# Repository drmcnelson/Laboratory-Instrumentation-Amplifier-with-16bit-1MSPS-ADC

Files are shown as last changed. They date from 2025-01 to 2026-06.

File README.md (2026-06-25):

# Laboratory Instrumentation Amplifier with bipolar inputs, 16bit 1MSPS ADC, SPI for Teensy, Arduino

<p align="center">
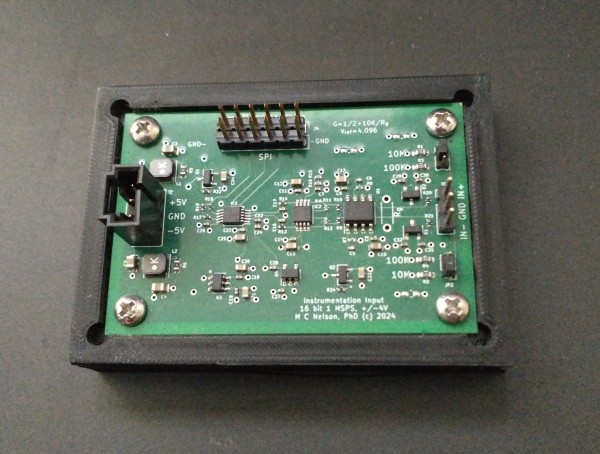
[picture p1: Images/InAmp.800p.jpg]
INA_actual

</p>

By [Dr M. C. Nelson](https://github.com/drmcnelson/Laboratory-Instrumentation-Amplifier-with-16bit-1MSPS-ADC),  [Copyright 2020-2026](LICENSE)

> **Important Build Note:** To ensure performance and alignment with the validated hardware and firmware, please build only from the **[Original Repository](https://github.com/drmcnelson/Laboratory-Instrumentation-Amplifier-with-16bit-1MSPS-ADC)**. 
>
>  For technical assistance or commercial inquiries, please contact me. I do my best to answer emails as volume allows.
<br>

---
### Table of contents
[Introduction](#intro)<br>
[1. Contents and instructions](#repo)<br>
[2. Design details](#design)<br>
[3. Spice model](#spice)<br>
[4. ADC sampling and timing](#timing)<br>
[5. Detailed part selection](#parts)<br>
[6. PCBWay sponsorship and acknowledgement](#ack)<br>

---
<br>

## Introduction

Instrumentation amplifiers ("INAs") are important for making sensitive precise stable voltage measurements with very high input impedance and strong noise rejection.
If you do research in the physical sciences or engineering or study electrical phenomena in biological systems, then you have probably used an INA.
They are a cornerstone of traditional instruments such as electrometers, and EKG machines, and laboratory studies in chemical physics, semiconductors, advanced materials, organo- and bio- electronics.

But, if you have used a traditional INA in your research, you may have noticed that they have certain limitations (which we are going to address in this design).
In particular, there is a well known trade-off where precision or sensitivity comes at the expense of some combination of bandwidth and impedance.
INAs are typically low bandwidth devices.
But there are interesting phenomena, for example involving charge processes on microsecond time scales, where high impedance measurements with a fast INA would be an especially useful tool.

This limitation in traditional INAs arises, at least in part, in two properties of amplifier chips; the input voltage noise density e<sub>n</sub> (V/√Hz) and the input current noise density i<sub>n</sub> (A/√Hz).
At a given bandwidth and impedance these contribute to the noise as *v*<sub>e,rms</sub> ≈ e<sub>n</sub>√f and *v*<sub>i,rms</sub> ≈ z<sub>n</sub> i<sub>n</sub> √f.
Note that both have a factor of root frequency but the current noise density is also multiplied by impedance.
We can think of a "noise resistance", R<sub>n</sub> = e<sub>n</sub>/i<sub>n</sub>.
When the amplifier input sees an impedance larger than R<sub>n</sub>, current noise dominates and noise increases more rapidly with bandwidth.
Low noise with high impedance and bandwidth requires low noise density with high noise resistance, alongside adequate bandwidth and slew.

Let's illustrate this with a numerical example. If we want 16 bit data for a signal of 1V, the noise (rms) should be around 10μV or smaller.
For a bandwidth of 1MHz, we need e<sub>n</sub> ≈ 10nV/√Hz.
And for an impedance of 10Mohm, we need i<sub>n</sub>  ≈ 1fA/√Hz.
That is, we need current noise density in the range of single digit fA/√Hz, or smaller.
It is challenging to find what we need in older INA chips (see [Table 5.8 in H&H AOE 3rd ed.](https://archive.org/details/the-art-of-electronics-3rd-ed-2015_202008/page/363/mode/1up)),
But there *are* newer Op Amps with ~10nV/√Hz and ~1fA/√Hz noise densities, >MHZ bandwidth and >10V/μs slew.
So, this is where a "roll your own" approach can be an advantage over older INA chips.

Another issue in traditional INAs is that they most often have single ended outputs.
The modern paradigm in high performance analog to digital converters (ADC) is increasingly to have differential inputs.
And, there is a large repertoire of high performance fully differential amplifiers (FDA) designed specifically to drive these differential ADCs.
Rather than run a single ended BNC across the lab to an analog input in a crate, nowadays we interface our high performance analog circuit over a short differential path to a high performance ADC co-located on the same board and export an all digital interface to an inexpensive microcontroller board or a computer.
The analog noise is well managed within a small area of the circuit board, and an all differential signal path helps control noise all the way to the ADC with its digital interface.

### About the INA and other contents of this repository:

In this repository we provide cad files and software source codes to make and operate an up-to-date instrumentation amplifier (INA) that can accommodate 10Mohm impedances with 16 bit precision at 1MSPS.
The host interface is a simple convert (CNVST) signal and SPI.
Asserting the "CNVST" line initiates conversion to digital and
after 700 nsecs, with CNVST low, a 16 bit SPI transfer retrieves the data.
The logic level for the SPI and CNVST are per the Vdd pin in the external connector and can be between 1.7V to 5.5V.
The SPI can be clocked as fast as 100MHz.
The INA board must be powered at -5V and +5V.
We provide a dual power supply for this, which we describe later.

We include an Arduino "sketch" (as source code) to operate the INA from a Teensy or Arduino microcontroller (MCU) board, and a Python program to provide an interactive interface to operate the instrument and record and display data in real time from a desktop or laptop computer.
The MCU board appears as a serial device to the computer with human readable commands and responses.
The source code has been compiled for and run on a Teensy 4, an Arduino UNO R4 and a STM32 Nucleo 144 (F7).
We prefer the Teensy for having the best SPI implementation and the fastest USB.

As described below, the basic operation of the device is simple and it should be easy to customize or crib from the source code or python code to integrate the INA into your experiment.

In the following we include some discussion of the design process, especially as related to part selection.
And we provide spice models that may help you check your changes, if you want to make any changes to the design.

For a more thorough discussion of the electrical topics mentioned here, the reader is referred to Horowitz, P., & Hill, W. (2015). The art of electronics (3rd ed.). Cambridge University Press. ISBN-10 0521809266.  Especially see Chapter 5 "Precision Circuits" and Chapter 8 "Low Noise Techniques".

### A word on the Spi Instrumentation Project:

Building instruments is an old tradition in science.  Many of the great advances were by scientists working with instrument makers or who were themselves great instrument makers.  In recent decades there is a different kind of pressure on academic science.  There seems to be less time or interest for learning those kinds of skills, compared to writing proposals to buy equipment.
Consequently doing science has become much more expensive and the sort of science someone gets to do increasingly becomes a function of where they are.
But like many things in nature, science is cyclic, and scientists are resourceful.
With the advent of low cost high performance MCU boards, 3-d printers and low cost CNC machines, there is now a growing community in DIY lab equipment.
But, there is still a roadblock when it comes to some of the more advanced design challenges.
Few are able to build a photon tagging system with picosecond timing from scratch, for example.
Our contribution, as long time instrumentation physicists is to fill in the gap to make higher end capabilities available to this new paradigm.
We believe that combining high end instrumentation circuits with the new generation in Arduino type MCU boards can be a powerful tool that can bring important capabilities to your lab and contribute to truly open science.

There is a sponsor button at the top of this repository.  Please do consider joining with us and contributing to our effort.

### Our sponsor for the INA - [PCBWay](https://www.pcbway.com/) 

We want to express special appreciation to PCBWay for sponsoring assembly of the first INA boards.  I enjoyed working them and we plan to work with PCBWay going forward.  Going back to PCBWay for the next designs and contributing to their community project forum, really is the best kind of praise that I can muster for any vendor.

On that note, we plan to post this design to the PCBWay community forum as our first experiment in this paradigm.  We are eager to see how it works out.

### Obtaining boards:

To obtain boards, the options include ordering a board through PCBWay per the above, or contact me and then click the sponsor button.
The parts cost at Digikey is USD 36 per board at this writing.
Preparing an order still takes a few hours of careful attention since we review everything and check for updates in the BOM each time.
<br>

<br>

---

## 1. Contents and Instructions:
In this repo you will find:
<ol type="a">
<li>
KiCad files - for a high performance INA with a 16 bit 1 MSPS ADC that can be used with a Teensy 4.x, UNO R4, Nucleo144 or other Arduino type MCU board.
</li>
<li>
Source code - to operate the INA with any of the above platforms to record voltages and waveforms in single, averaged, clocked or triggered data acquisition modes, implement a set of human readable commands and transfer data over USB.
</li>
<li>
Python code - class library and utility program that runs on a desktop or laptop to operate the INA-MCU, view data in realtime and save data to disk files.
</li>
<li>
SPICE models - in LTSpice for the complete circuit and including a model for the ADC.
</li>
</ol>

### a) Fabrication
In the KiCAD files directory you will find a zip file with gerbers, drill and placement files, and a BOM.  These are easily regenerated from the KiCAD files.  If you are not familiar with ordering PCBs or assembly, the support team at PCBWay will guide you through the process.  Alternatively, you can sponsor a fabrication run and get a board.  Contact me for more information about this.

### b) Controllers
You may want to use the INA with one of our controllers.
Please see our new [Teensy 4.0 based controller here (rev3)](https://github.com/drmcnelson/Instrumentation-Controller-T4.0-Rev3) 
and our [T4.1 based controller here](https://github.com/drmcnelson/SPI-Instrumentation-Controller-T4.1).
We recommend these over other Arduino type MCU boards because of (a) the faster processor, (b) faster USB, (c) native 16 bit transfer capability already built into the Teensy SPI library, and (d) managed power.

### c) Power requirements and recommended power supply
The INA requires a -5V,+5V power supply.
The repo for our [+/-5V instrument power supply is  here](https://github.com/drmcnelson/Dual-pos-neg-5V-Supply-from-USB-power)
The power architecture of the INA assumes the the board is powered by this power supply.
The power supply in turn is normally powered from the filtered +5V power connector provided on the controller although it can alternatively be powered directly from USB

### d) The complete setup with controller and recommended power supply.
The following shows a complete setup with the INA, T4 based controller and power supply.  Notice the power supply is powered by the +5V connector on the controller and then powers the INA.   The INA is connected to the controller by a 12 pin (2x6) ribbon cable.

<p align="center">
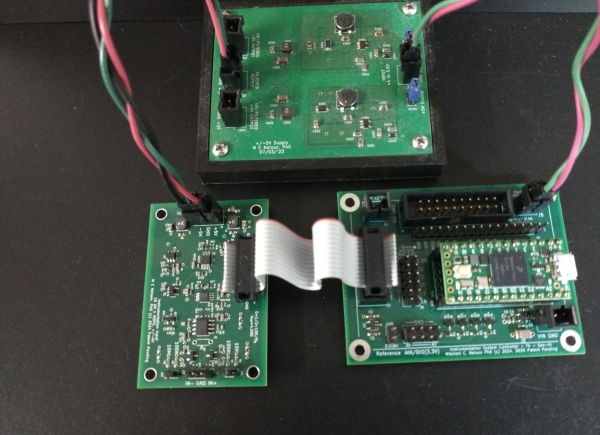
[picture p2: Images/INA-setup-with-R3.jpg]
INA_setup

</p>

Here we show the input connectors. The instrumentation amplifier can be used as a single ended or differential input.  Input impedance is jumper selected as will be discussed.

<p align="center">
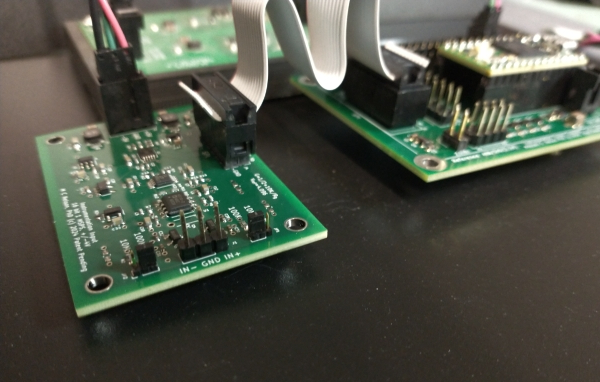
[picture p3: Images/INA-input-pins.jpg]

</p>

### e) Input range and bandwidth
The range at each side of the differential input is -4V to +4V.
Full scale for the differential signal is therefore 8V.
Spectral response is flat from DC.
There is a low pass filter with time constant at the Nyquist limit for the 1MHz sample rate.

### f) Increasing gain
Gain can be increased by adding the resistor Rg.
There is a thru-hole footprint for this part located between the input header and the first Op Amp chip.
The gain equation is G = 1/2 + 10K/Rg.
Rg = 100 will give you a gain of 100.5.
With a gain of 100, the full scale range on each side of the differential input is effectively 40mV and the full scale differential signal is 80mV.
Larger inputs will clip since the rails for the Op Amps are just a little past -4V and +4V.

### g) Jumpers, selecting input impedance
There are three pin jumpers adjacent to each side of the differential input.
These allow you to select a 10M or 100K shunt to ground.
With no jumper installed the input impedance is that of the non-inverting input of the Op Amp.
It is important to have some path to ground, whether it is through the shunt resistor or the sample, rather than leave the input to drift off to one of the rails.

### h) Thermistor and measurements with voltage divider
You might use the internal 100K shunt with an external 100K thermistor to make accurate temperature measurements, or with an external resistor to form a divider to look at larger voltages.

The setup with a thermistor would look like the following where Vin is a known constant voltage and the internal resistor is selected by the jumpers as described above.  The controller has a high precision voltage reference output that you can use for this.

<p align="center">
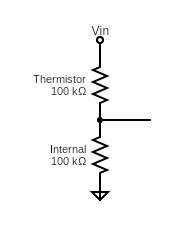
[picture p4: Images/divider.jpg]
divider

</p>

The setup with a divider would look similar to the above, though the external resistance might be considerably larger.
If you use a divider to measure large voltages, be very careful that the resulting voltage at the divider is within 4V.

Keep in mind also that Johnson (thermal) noise density for a resistor is about 0.13√R in units of nV/√Hz.
For a 16 bit precision on ±4V, 1LSB corresponds to 122μV. 
For 1Mohm and 1MHz the Johnson noise is 130uV.
So a 10:1 divider using the internal 100K and a 900K external can be okay.
With larger resistors more bits are used up for noise.
<br>

### i) Specs
<table style="width:60%;margin-left:30px">

<th>
Specifications
</th>
<tr>
<td style="padding-left:1rem">
 Input range
</td>
<td>
±4V each (±8V differential)
</td>
</tr>

<tr>
<td style="padding-left:1rem">
Input Impedance
</td>
<td>
10M, 100K, 1T (open), 20pF
</td>
</tr>

<tr>
<td style="padding-left:1rem">
Sampling rate
</td>
<td>
1 MSPS
</td>
</tr>

<tr>
<td style="padding-left:1rem">
Precision
</td>
<td>
16 bit
</td>
</tr>

<tr>
<td style="padding-left:1rem">
Digital Noise
</td>
<td>
+/-1 LSB
</td>
</tr>

<tr>
<td style="padding-left:1rem">
External Interface
</td>
<td>
CNVST, SPI to 100MHz, VDD 1.7V to 5.5V
</td>
</tr>

<tr>
<td style="padding-left:1rem">
Analog Power
</td>
<td>
-5V, +5V
</td>
</tr>
</table>

<br>
<br>

---

## 2. Design details

### a) Architecture

The traditional INA architecture is shown in the following diagram.
The input stage is a pair of Op Amps tied together by the resistor network R1-Rg-R1. The second stage is a difference amplifier with single ended output.
The overall gain is G = (1 + 2R1/Rg)(R3/R2).
This is a well studied circuit, you can read about it
in the textbook by Horowitz and Hill cited in the introduction,
or at [Wikipedia](https://en.wikipedia.org/wiki/Instrumentation_amplifier)
or in the many vendor application notes on the subject.

<p align="center">
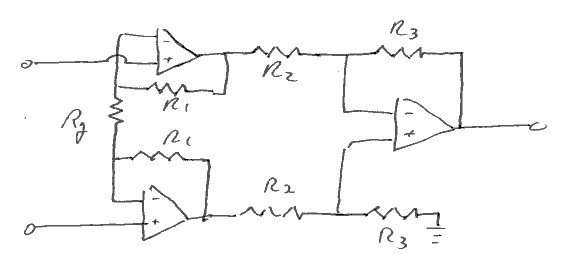
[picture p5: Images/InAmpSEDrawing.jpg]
INASEdrawing

<br>
<caption>
INA in the traditional configuration has single ended output.
</caption>
</p>

The following circuit diagram shows the INA architecture that we want to use for our circuit.
The differential amplifier is replaced with a fully differential amplifier (FDA) and the output from the FDA is interfaced to the differential input of a high performance ADC.
The ADC communicates with the outside world, for example a Teensy board or Arduino, over SPI.

<p align="center">
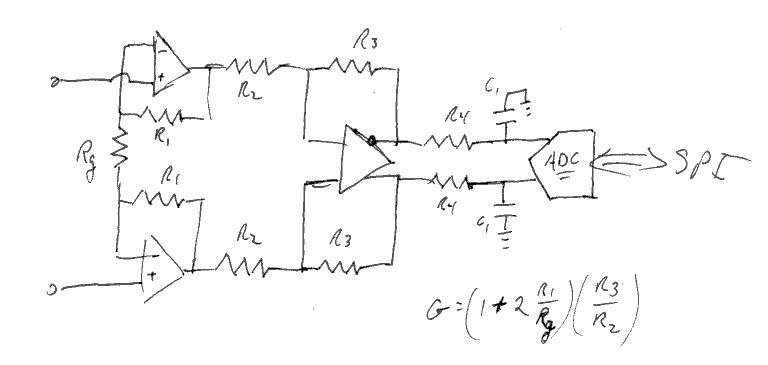
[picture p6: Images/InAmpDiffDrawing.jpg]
INA-Single

<br>
<caption>
INA with differential output stage and differential ADC.
</caption>
</p>

### b) Component selection, in brief

For our Op Amp selection, key parameters include the input current noise density i<sub>n</sub>, input voltage noise density e<sub>n</sub>, slew rate, and power supply rejection ratio (PSRR) as follows:
<ul>
<li>
Voltage noise density should be in the range of nV/√Hz for 16 bit precision with 1MHz bandwidth.
</li>
<li>
Current noise density in the range of single digit fA/√Hz is a pre-requisite for 16 bit precision with order 10 Mohm input impedance and 1 MHz bandwidth.
</li>
<li>
Slew rate in the range of 10V/us or better is a requirement for being able to study phenomena that appear as steps or transients on a μs time scale.
</li>
<li>
Power supply rejection ratio above 60dB is a requirement for the Op Amp and for the FDA, with the recommended power supply.  This is discussed later in further detail for the ADC.
</li>
</ul>

For the design provided here, the input stage is an ADA4510-2,  which is a dual Op Amp with i<sub>n</sub> = 4fA/√Hz, e<sub>n</sub> ≈ 5nV/√Hz, maximum slew = 19V/μs and PSRR 140dB.
As noted above, at 10Mohms at 1MHz, our noise is 40uV.

For the FDA, all of the above are important except that the current noise requirement is relaxed since the FDA sees low source impedances in the outputs from the first stage.  We choose an LT1994, which exceeds the front end specs with e<sub>n</sub> ≈ 3nV/√Hz and slew at 85V/μs.  Its PSRR is 105dB.

Both the ADA4510 and LT1994 are rail to rail parts.

For the ADC, our requirements include 16bits, 1MSPS, differential inputs, reference voltage, input range to 4V on each side of the differential input, SPI for the interface to the MCU, and it should accommodate 3.3V or 5V logic levels to be able to interface to a wide range of Arduino boards.  The precision and speed puts us in the range of a SAR type ADC.
The flexibility in logic levels narrows the selection somewhat.
It is also important to closely check performance specs including latency, missing codes, SNR, INL and DNL.

In this design we choose the Microchip MCP33131D as a 16 bit differential input 1MSPS SAR type ADC with SPI that can accommodate the required logic levels.
The SNR is listed as 91.3 dB which translates to a noise level of about 1 LSB.
This is one spec where the corresponding TI part might seem marginally better, but it comes at the cost of only accepting 3.3V logic.

For a voltage reference we select the REF3440 which has 3.8uV/V noise, low dropout at 100mV and is recommended for 16bit to 18bit ADCs.

### c) Interfacing to the ADC

SAR type ADCs, like most analog input architectures, feature a switched sampling capacitor.
A simplified version is as follows.
The switch closes connecting the input to the sampling capacitor.
The resistor represents the overall resistance inside the input including the closed resistance of the switch.
The capacitor then charges to the voltage at the input.
The switch opens and the SAR reads the voltage and converts it to a digital representation.

<p align="center">
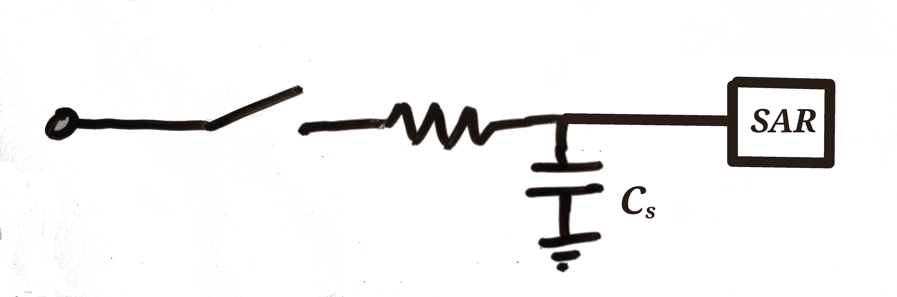
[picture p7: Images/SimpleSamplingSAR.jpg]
SimpleSampling

</p>

There are two interrelated challenges in driving a switched capacitor network; providing a charge reservoir for the in-rush current when the switch closes, and assuring that the capacitor charges quickly enough or that there is sufficient time in the sampling window, for the sampling capacitor to come within 1 LSB of the input voltage.
The recommended strategy is to provide a charge reservoir in the form of an external capacitor, and a buffer amplifier to charge the reservoir, as follows.

<p align="center">
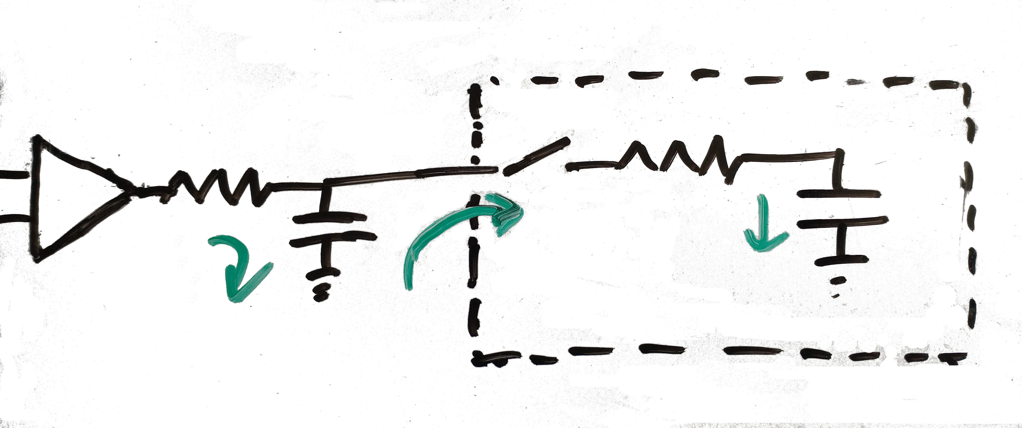
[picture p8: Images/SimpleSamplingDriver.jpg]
SimpleSampling

</p>

The trick in the above, is that these two capacitors charge on different time scales.
The sampling time allowed for charging the internal sampling capacitor is usually smaller than the period between samples.
The buffer has to supply current on the slower time scale to keep the reservoir charged, but it is the reservoir that absorbs the large fast spike when the switch closes.
   
The design process for the interface to the ADC is then:
   1) Choose the external capacitor to be a few times larger than the internal capacitor, then
   2) Choose the external resistor so that the time constant is faster than 1/2 of the sampling rate, and then
   3) Choose an Op Amp that is (a) able to deliver current equal to the full scale voltage divided by the external resistor, and (b) has a maximum slew that is much larger than the full scale voltage divided by the sampling period.
 
 With that high level view, let's take a look at our ADC.

The datasheet for the MCP33131D ADC provides the following equivalent circuit for its input.

<p align="center">
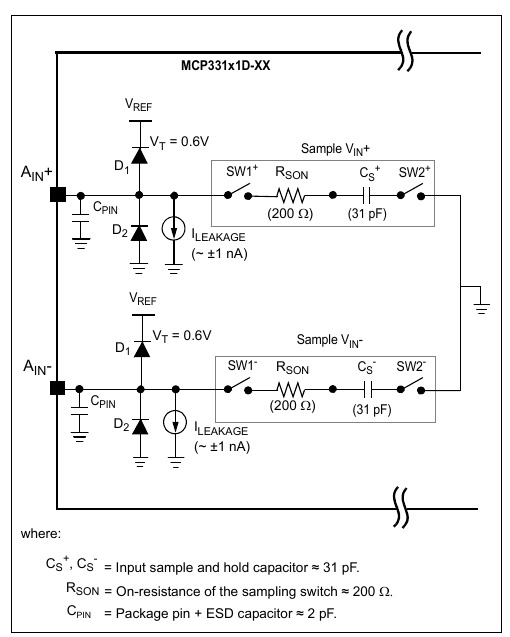
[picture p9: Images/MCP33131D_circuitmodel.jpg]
MCP33131Dmodel

</p>

Here we see a switched capacitor network for each side of the differential input.
There seems to be a novelty in that the sampling circuit is represented with a second switch to isolate the capacitor between samples.
Manufacturers often describe the state of the sampling capacitor as "unknown" between sampling events.
Here the intent seems to be a little more specific.
But in actuality there has to be some loss of charge between sampling events even if very small.

In practice, when you model a switched sampling capacitor network in SPICE, you always include a second switch to discharge the capacitor between samples.
If your driving circuit will get the sampling cap to the right voltage within the sampling window coming from 0 each time, it should be okay when you deploy it in the actual device.

Meanwhile, we have some important takeaways from the equivalent circuit.
The capacitor sees a time constant of 6.2 nanoseconds provided there is minimal impedance seen in the driving circuit, and we need something much larger than 30pf in the external capacitor.

---

## 3. SPICE model

For purposes of designing and modeling a circuit to drive an ADC, standard practice as mentioned above, is to use a model similar to the following for the switched sampling capacitor network:
<p align="center">
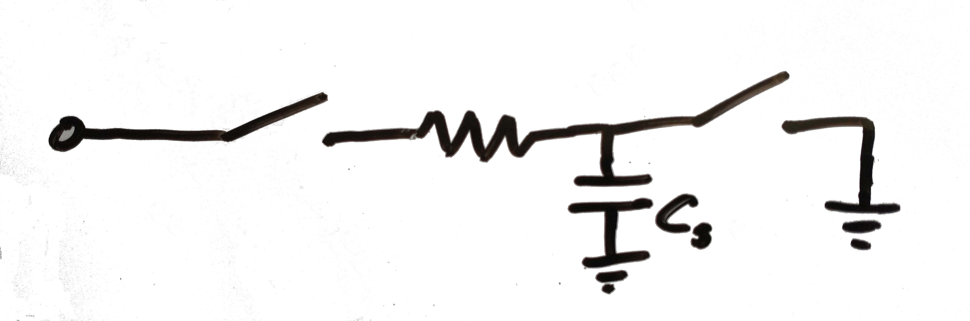
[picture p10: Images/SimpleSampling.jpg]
SimpleSampling

</p>

In other words for purposes of modeling the sampling input, we discharge the capacitor between samples. 
A circuit that can drive the sampling cap from 0 to within 1LSB of the input voltage within the sampling period, should be sufficient for any reasonable state of the cap in operation.

The following shows our INA circuit with the equivalent circuit for the sampling input from the datasheet for the ADC.
External to the ADC, on each of the inputs, we have a resistor and capacitor to act as a charge reservoir for the sampling capacitor.
Internal to the ADC sample and hold, we have the switches as shown in the equivalent circuit from the datasheet.
Recall that this ADC isolates the capacitor between sampling windows.

<figure>
<p align="center">
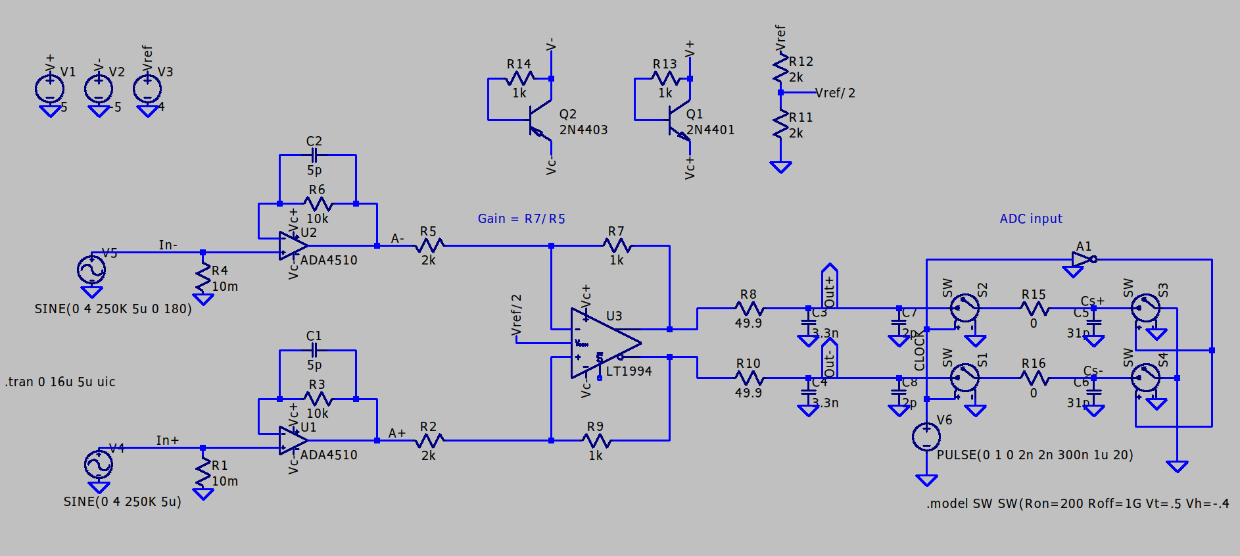
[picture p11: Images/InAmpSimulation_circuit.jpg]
circuit

<br>
<caption>
INA circuit model for SPICE,
</caption>
</p>
</figure>

The following shows (a) the voltages at the positive and negative inputs of the two front end amplifiers in two shades of green, and (b) the voltages at the two outputs of the FDA in two shades of blue.
As required for the ADC, the inputs are transformed from a bipolar range from -4V to +4V, to a unipolar range from 0V to 4V.

<p align="center">
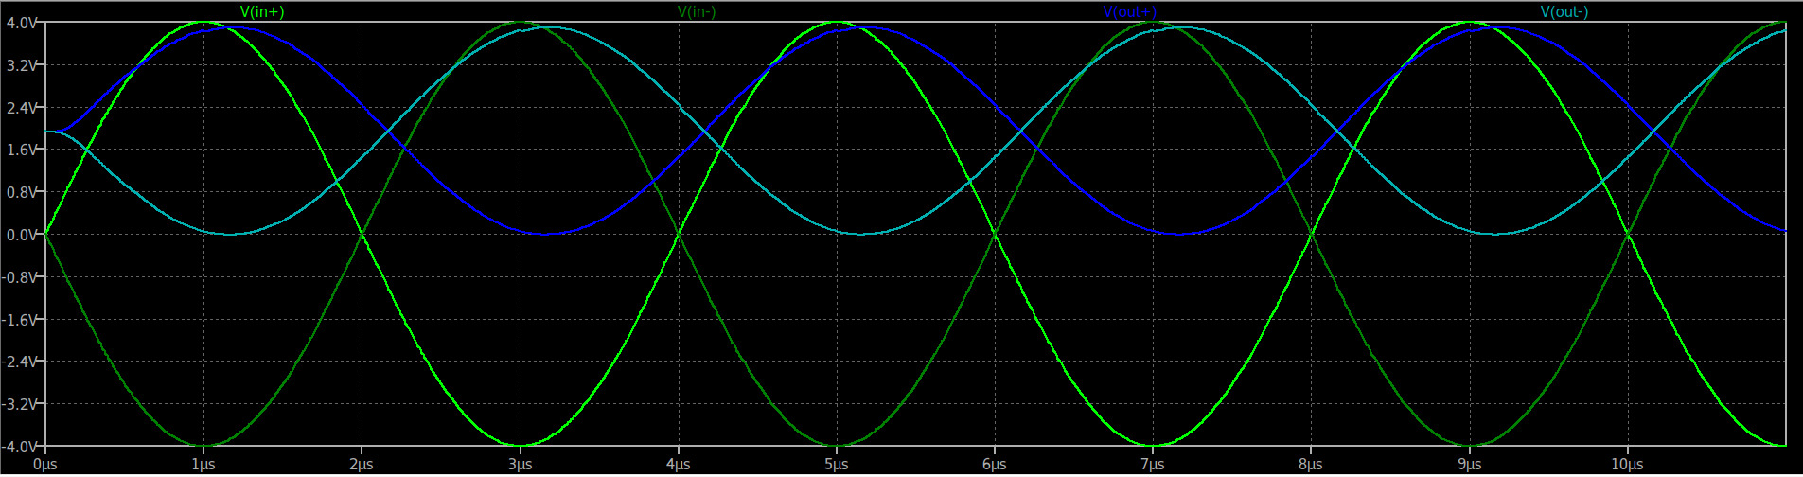
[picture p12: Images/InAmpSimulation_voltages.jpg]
voltages

<br>
<caption>
Voltages at inputs to the front end (green) and at the output
s of the FDA (red and lavender).
</caption>
</p>

The following shows (a) the output from one side of the FDA (blue), (b) the voltage on the sampling capacitor (red), (c) switching clock for the sampling network (grey).
We see that voltage on the sampling capacitor easily tracks the input to the ADC.

<figure>
<p align="center">
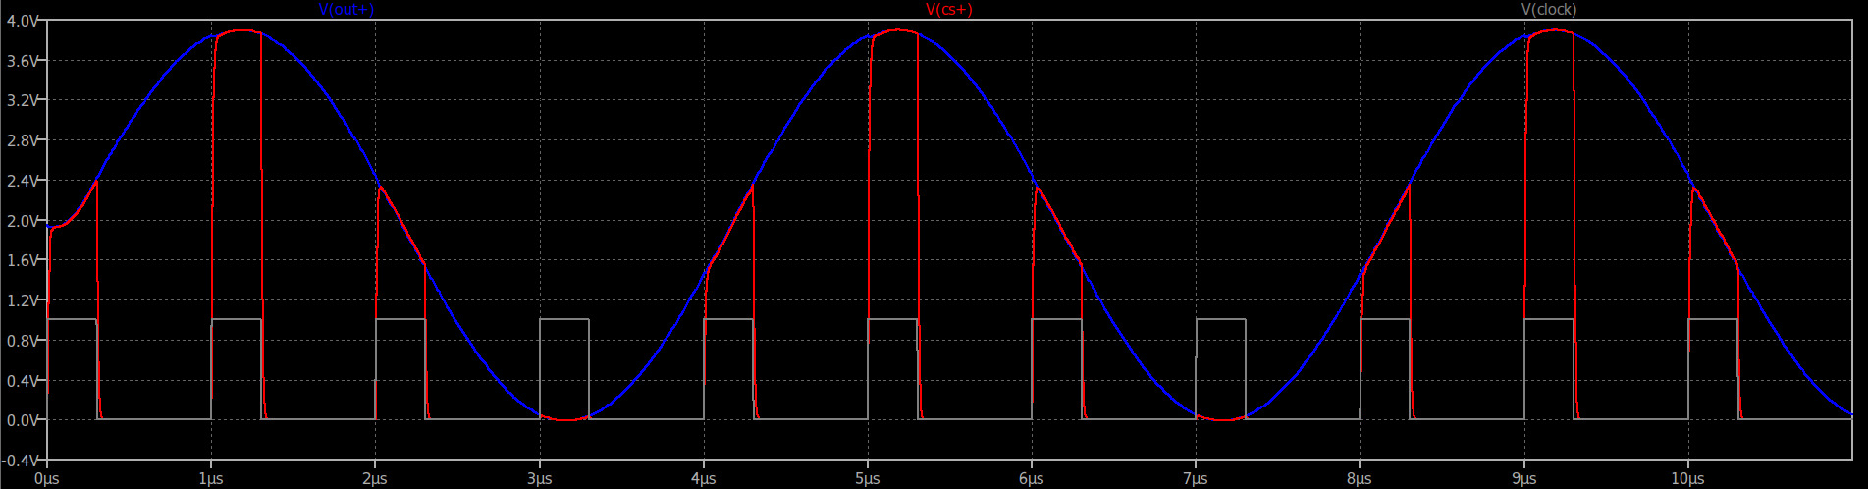
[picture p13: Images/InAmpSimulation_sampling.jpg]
sampling

</p>
<br>
<figcaption>
Positive side output from the FDA (blue), voltage on the sampling capacitor (red), and sampling clock (grey).
</figcaption>
</figure>

Here we add traces for the current through the sampling cap (green) and the capacitor services as the external charge reservoir (gold).
Notice the current spike through the sampling capacitor.
We see this is supplied by the external capacitor acting as charge reservoir, which slowly charges between switch events.
Notice also that there is no discernible spike in the output from the FDA.
So the charge reservoir is working as it is supposed.
On each sampling cycle, the sampling capacitor is able to rapidly come to the voltage presented at the input.

<figure>
<p align="center">
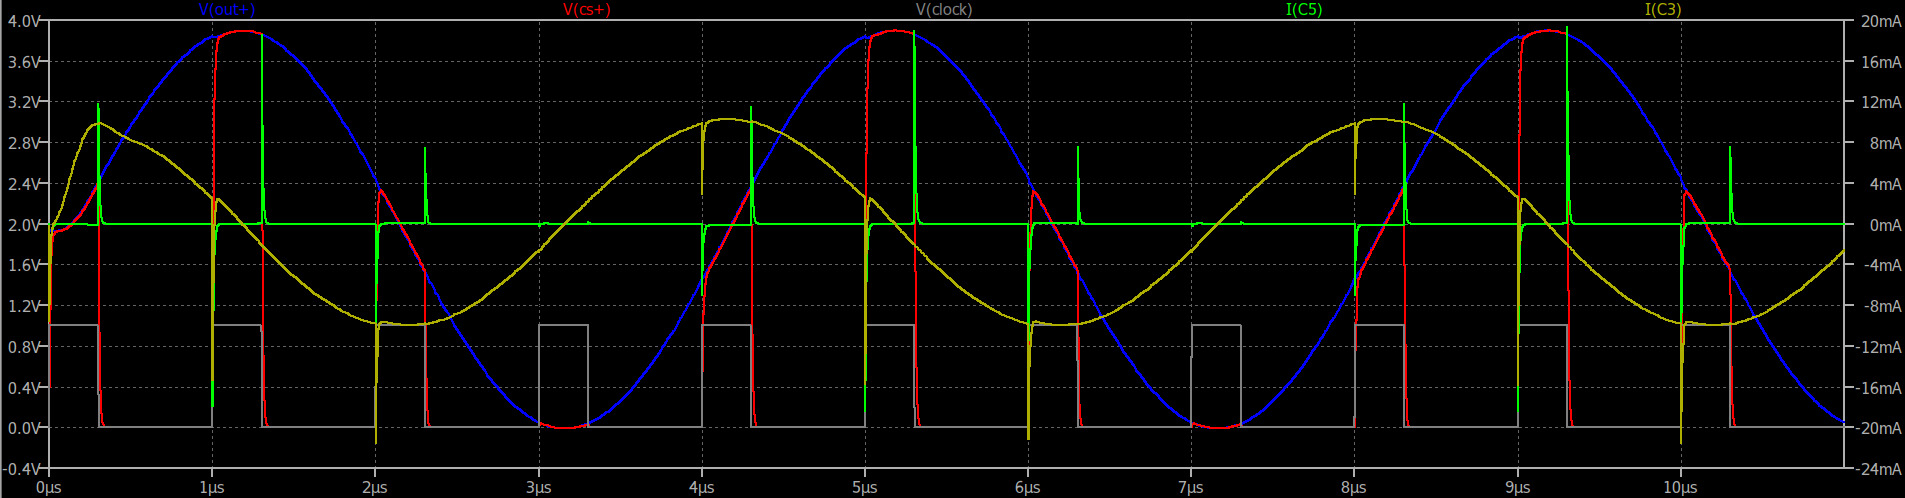
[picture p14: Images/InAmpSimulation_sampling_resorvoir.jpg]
sampling

</p>
<br>
<figcaption>
Positive side output from the FDA (blue), voltage on the sampling capacitor (red), current through the sampling capacitor (green), current through the external reservoir capacitor (gold) and the sampling clock (grey).
</figcaption>
</figure>

It is good practice to always check your ADC designs this way.  Find the equivalent circuit in the datasheet and implement it in terms of the capacitances and resistances and make sure you are driving it correctly.

Now, we have two more very important aspects of our circuit design to check, spectral response and noise.
We will look at these at the input to the ADC.
For completeness the following is our SPICE model modified for these analyses with large source impedance on each side of the differential input.

<figure>
<p align="center">
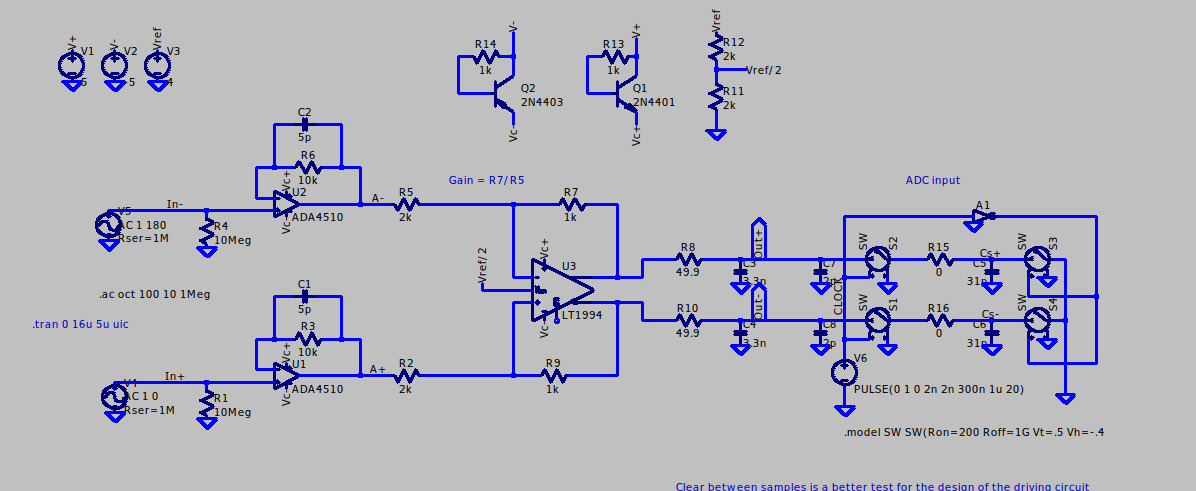
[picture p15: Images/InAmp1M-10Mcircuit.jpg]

</p>
<figcaption align="center">
Spice model with large source impedances.
</figcaption>
</figure>

The following shows the spectral analysis.  If you do not know how to do this in LTSpice, there is [a short tutorial video here](https://youtu.be/fziUQaVQxA4?feature=shared)
Here we see that our response is flat to 100kHz and then rolls off only slowly reaching -1.4dB and a 45 degree phase shift at around 1MHz.
If you want a more aggressive roll off you can substitute the caps in the feedback networks in the front end, or use larger caps for the charge reservoir in front of the ADC.

<figure>
<p align="center">
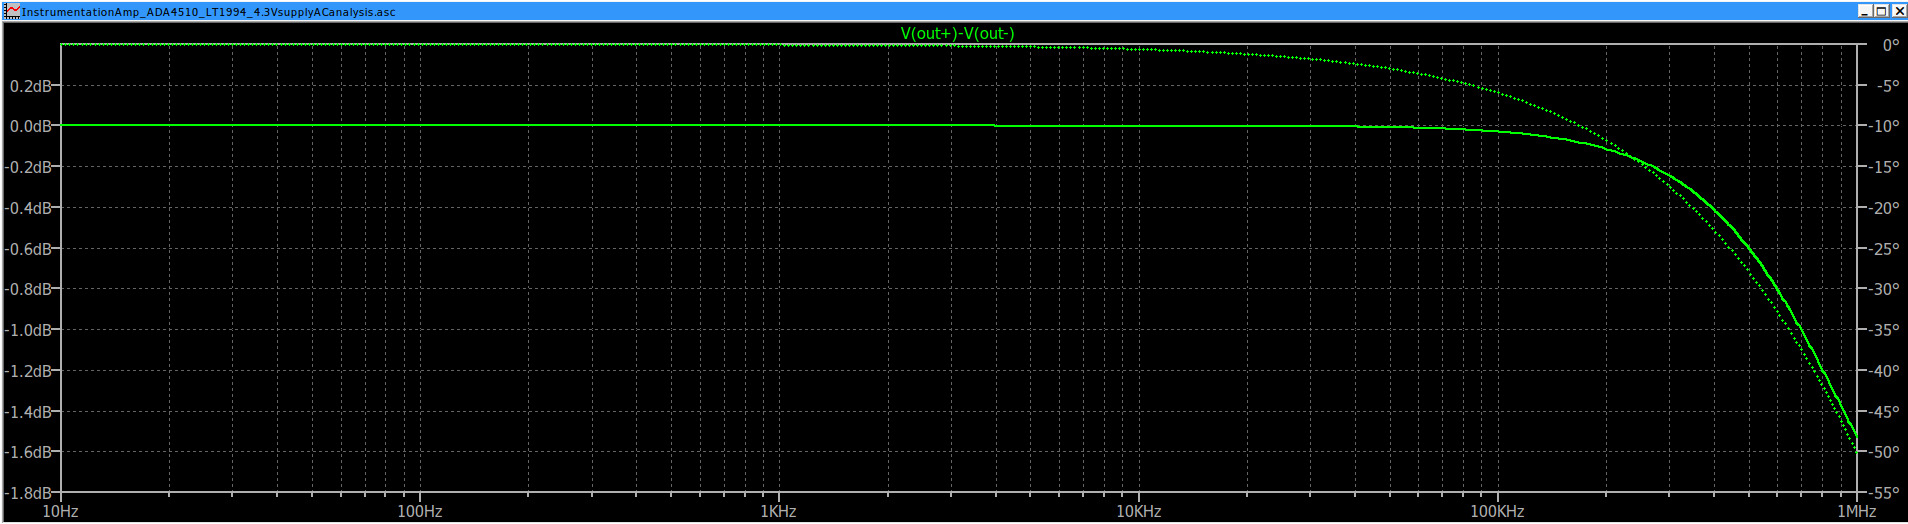
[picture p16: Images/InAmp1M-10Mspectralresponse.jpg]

</p>
<figcaption align="center">
Spectral response.
</figcaption>
</figure>

The following shows the noise analysis. As above, you can [see how to do this in LTSpice in the short tutorial video here](https://youtu.be/hBsBl27etYs?feature=shared).
https://youtu.be/hBsBl27etYs?feature=shared
 The noise density remains well below our target for 16 bit precision throughout the entire spectral range, even with a 1M source impedance at the input.

<figure>
<p align="center">
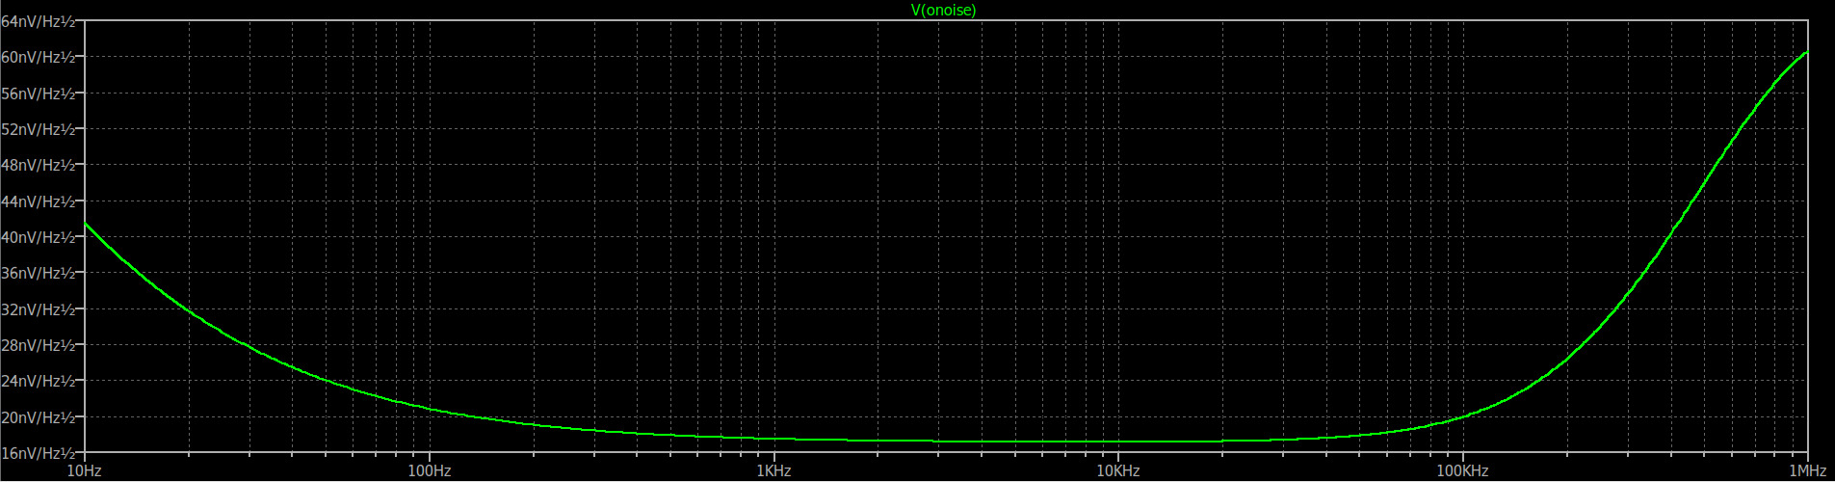
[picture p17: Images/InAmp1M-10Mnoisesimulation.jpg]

</p>
<figcaption align="center">
Noise density.
</figcaption>
</figure>

So, it appears that the design meets our goals,  We expect to be able to make 16 bit 1MSPS measurements with high source impedance.
Spectral response is flat and then rolls off by less than 2dB above 100KHz and noise is under our 120uV requirement throughout the spectral range.

---

## 4. ADC Sampling and Timing

Voltage sampling is controlled by the CNVST pin in the double row header.  Assertion of this pin effectively marks the end of the sampling interval, causes the most recent level at the input to be converted to digital and made available for retrieval by the host.  The timing relationship between CNVST and the sampling window is important if the ADC sampling is to be synchronized to another instrument or specific external events.

The ADC, a MCP33131D-10, is described in detail in the datasheet found [here](https://ww1.microchip.com/downloads/en/DeviceDoc/MCP33131D-Data-Sheet-DS20005947B.pdf).
Figure 6-10, page 37, reproduced below, provides a high level view of the sampling, conversion and transfer cycle.  For detailed timing information see Figure 1-1, page 9 and related text.

In the diagram we see that when the CNVST pin is asserted, the inputs are latched and the ADC begins converting the latched signal, which represents the most 300nsecs at the inputs.  After  700nsecs conversion is complete and the data can be read over SPI by a 16 bit transfer.  The transfer can be shortened by asserting the CNVST pin again before the transfer is complete.  The maximum sample rate is 1MSPS for 16 bit with a 60MHz SPI or 800KSPS with a 30MHz SPI.
The data is a 2's complement 16 bit integer. It is easily converted to an unsigned 16 bit integer by toggling the high order bit.

<p align="center">
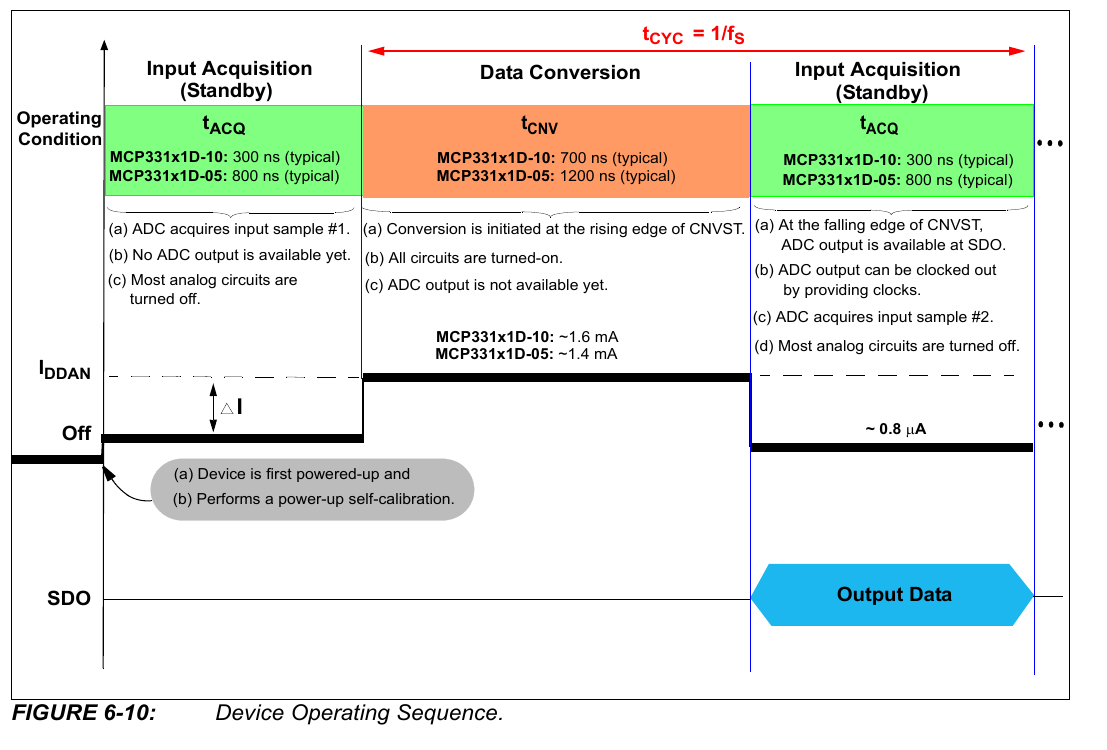
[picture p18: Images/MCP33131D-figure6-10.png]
ADCoverview

</p>

---

## 5. Part selection in more detail

In this section we discuss one of the more important design choices, the input range, and then take a more detailed look at electrical characteristics and part selection.
This may be helpful if you want to modify the design.
Over-designing can present compromises and limitations just as under designing might.
If your requirements are sufficiently different from ours, the part selection process might lead you to a choice that is better for you.

Let's begin.

### a) Choosing the operating range

If we had a specific research goal in mind, we would consider the phenomena we are going to study, set the voltage range accordingly and proceed with the design from there.
Designing for a general case with a spec that reads "I want to use this for anything", is always far more difficult and laden with ambiguities.  A practical spec might be "what is the best we can do?"

As it turns out, 4V can be a convenient range with 5V as the primary power source.
For scientific applications, it is preferable to have a bipolar input, for example -4V to 4V rather than unipolar from 0 to 4V.
If I want to report a measurement as yielding zero volts (0V), most often I have to be able to read voltages above and below 0V.
And, if I want to study a phenomenon over a range that spans 0V, i.e. from negative to positive, then most often I want to do that all in one go, not half at a time.

As described earlier, for an INA any reasonable range is not  very constraining.
We can increase gain to zoom-in to a smaller range or add a series resistor to zoom-out to a larger range.
The bipolar choice has a more significant effect in that any unipolar measurement is inherently half-scale.

### b) What noise level do we need to achieve?

Given that we have chosen 16 bit precision, our noise level should be not very much larger than 1 part in 2<sup>16</sup> (1LSB) relative to our full scale input.
The ADC will have 1LSB of noise almost no matter what we do, because that's the physics of digitizing something.
Taking 4V as full scale our noise goal is 4V/65535 ~ 61μV at the input to the ADC, or 120μV at the input to the INA.

### c) Input voltage and current noise densities and the impedance bandwidth tradeoff.

As we discussed in the introduction, noise at the input to an Op Amp is described in terms of (a) its input voltage noise density e<sub>n</sub> (V/√Hz)
and (b) its input current noise density i<sub>n</sub> (A/√Hz).
We discussed this in the introduction.

Let's see how this works for the ADA4510.  This is an Op Amp designed for high precision and high input impedance.
The datasheet (Rev 0 is dated 7/2023), lists e<sub>n</sub> ~ 5nV/√Hz and i<sub>n</sub> ~ 4fA/√Hz.
With current noise density in the range of single digit fA/√Hz, our impedance threshold for current noise is 1Mohm,
But the noise is still small.
At 10Mohm and 1MSPS we are still doing well relative to our noise requirement for 16 bit measurements.

For comparison, the popular INA chip, the LT1167 (RevB datasheet dated 2011) has e<sub>n</sub> ~ 7.5nV/√Hz and i<sub>n</sub> ~ 60fA/√Hz above 100Hz.
That puts the impedance threshold at about 100Kohm.
For a large source impedance the LT1167 has to give away a lot of bandwidth compared to what we might expect with a well designed front end based on the ADA4510.

### d) Maximum slew rate and bandwidth

For an Op Amp, speed can be described by its bandwidth or gain bandwidth product (GBP) and by its maximum slew (V/μs)
It is possible to have a very large bandwidth, but be limited by the maximum slew.
For example, the LT1167, can support a gain of 1 with a 1MHZ bandwidth, but its maximum slew is 1.2V/μs.
The ADA4510 has a 10MHz gain bandwidth product, and its maximum slew rate is 19V/μs.
They both seem to have better than 1/2MHz bandwidth, but the ADA4510 can actually slew a full range (-4V to 4V) signal at that speed.

### e) Input capacitance

Looking again at the input characteristics, we might notice that there are two capacitances listed, C<sub>INDM</sub> the differential mode capacitance, and C<sub>INCM</sub> the common mode capacitance.a
The following diagram explains the terminology.
You can think of these quantities as the capacitances between the input pins and between each pin and its rail (or AC ground as shown).

<p align="center">
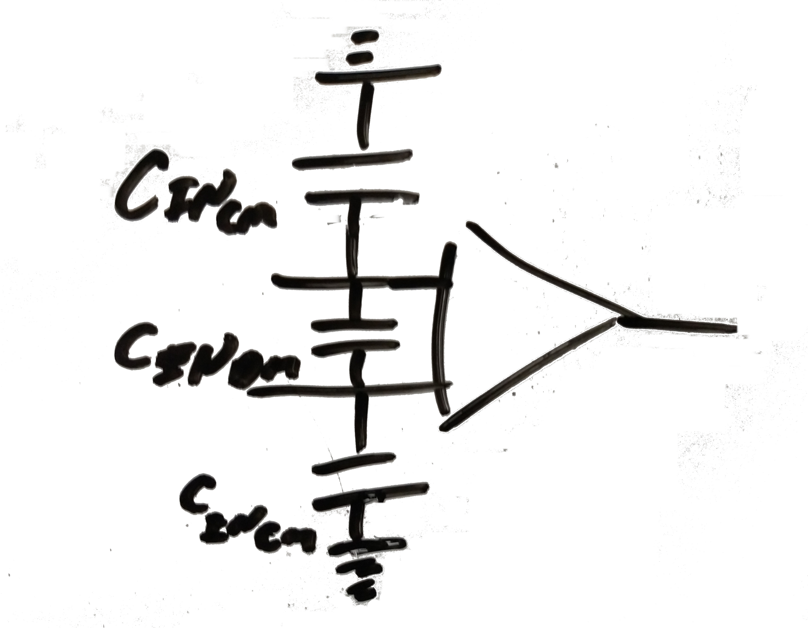
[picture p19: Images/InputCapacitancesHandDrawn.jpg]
InputCapacitances

</p>

We will mention here that the ADA4510 we have C<sub>INDM</sub> 20pF and  C<sub>INDM</sub> = 2pF, and the LT1167 has C<sub>INDM</sub> 1.6pF and  C<sub>INDM</sub> = 1.6pF.
But the situation is a little more complicated.
The best way to see what is going on is to run a spice model for the spectral response.
We will show that in a moment.

N.B. When impedances are large, small capacitances become even more important.  Pay careful attention to recommendations in the datasheets about layout around input pins for all of the active parts in the design.

### f) Power supply rejection ratio.

Almost any active part used in an analog circuit has a power supply rejection ratio PSRR listed in its datasheet.
The name of the game, is that the PSRR for each part involved in the analog chain acting on the the noise level of whatever is powering it, has to be better than the noise level that we are trying to achieve in our design.   For a 16 bit board, we need an SNR better than 96dB.

The recommended power supply is posted [here](https://github.com/drmcnelson/Dual-pos-neg-5V-Supply-from-USB-power).
This is based on the LT1930 and LT1930, the datasheets indicate output noise of about 1mV.   For our amplifier chips a PSRR of even 60dB will get us into the μV range that we need for our noise specs. PSRR for the ADA4510 is 140dB, so we're in pretty good shape.
Our FDA an LT1994 has a PSRR of 105dB.  We're still good.

The ADC is an MCP33131D and is powered from a 1.8V LDO TPS72218 with noise level 90μV.
A PSRR at -20dB reduces to 9μV or less than 1LSB in the digital output, and vref is a REF3440 with noise level 3.8μV/V or 16μV, again significantly less than 1LSB.

### g) On rail to rail amplifiers

Our 4V range means that we need an Op Amp and FDA that are rail-to-rail with regard to both inputs and outputs and with a common mode that goes to at least 1/2 of the rail.

Some R-R are more R-R than others.
It is important to check the datasheet carefully to make sure the part you are selecting has adequate input, output and common mode ranges.
Traditional INA are generally not R-R.

Our ADA4510 does go right to the rails (from 0.15V above Vs- all the way to Vs+). 
The LT1994 is also rail to rail in terms of inputs and outputs but its common mode level has to be at least 1 volt from either rail.
That is okay for our case.  We are using the common mode control pin and setting it to the midpoint of the two rails.

---

## 6. Acknowledgement

### Our sponsor - [PCBWay](https://www.pcbway.com/) 

We want to express special appreciation to PCBWay for sponsoring assembly of the first INA boards.  The work product and materials are quite good, and the staff were helpful way above and beyond expectations.  I look forward to working with PCBWay again.

Going back to PCBWay for the next designs and contributing to their community project forum, really is the best kind of praise that I can muster for any vendor.

On that note, we plan to post this design to the PCBWay community forum as our first experiment in this paradigm.  We are eager to see how it works out.

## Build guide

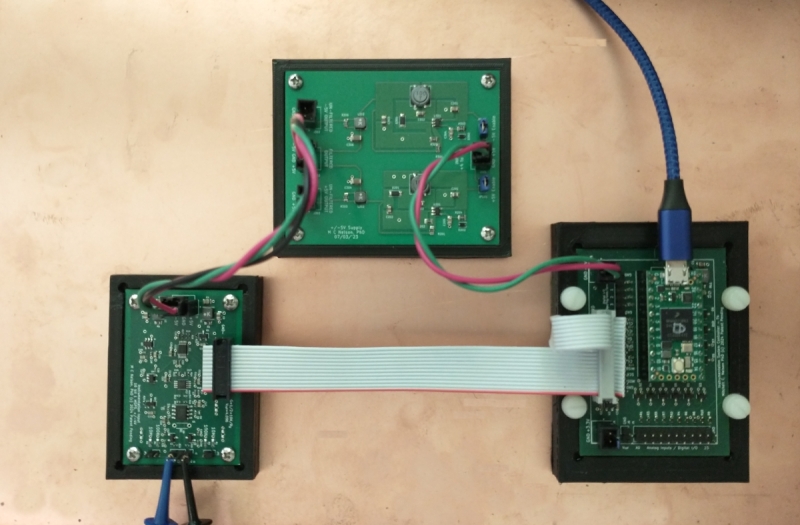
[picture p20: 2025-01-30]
Images/InAmpSetup.p800.jpg

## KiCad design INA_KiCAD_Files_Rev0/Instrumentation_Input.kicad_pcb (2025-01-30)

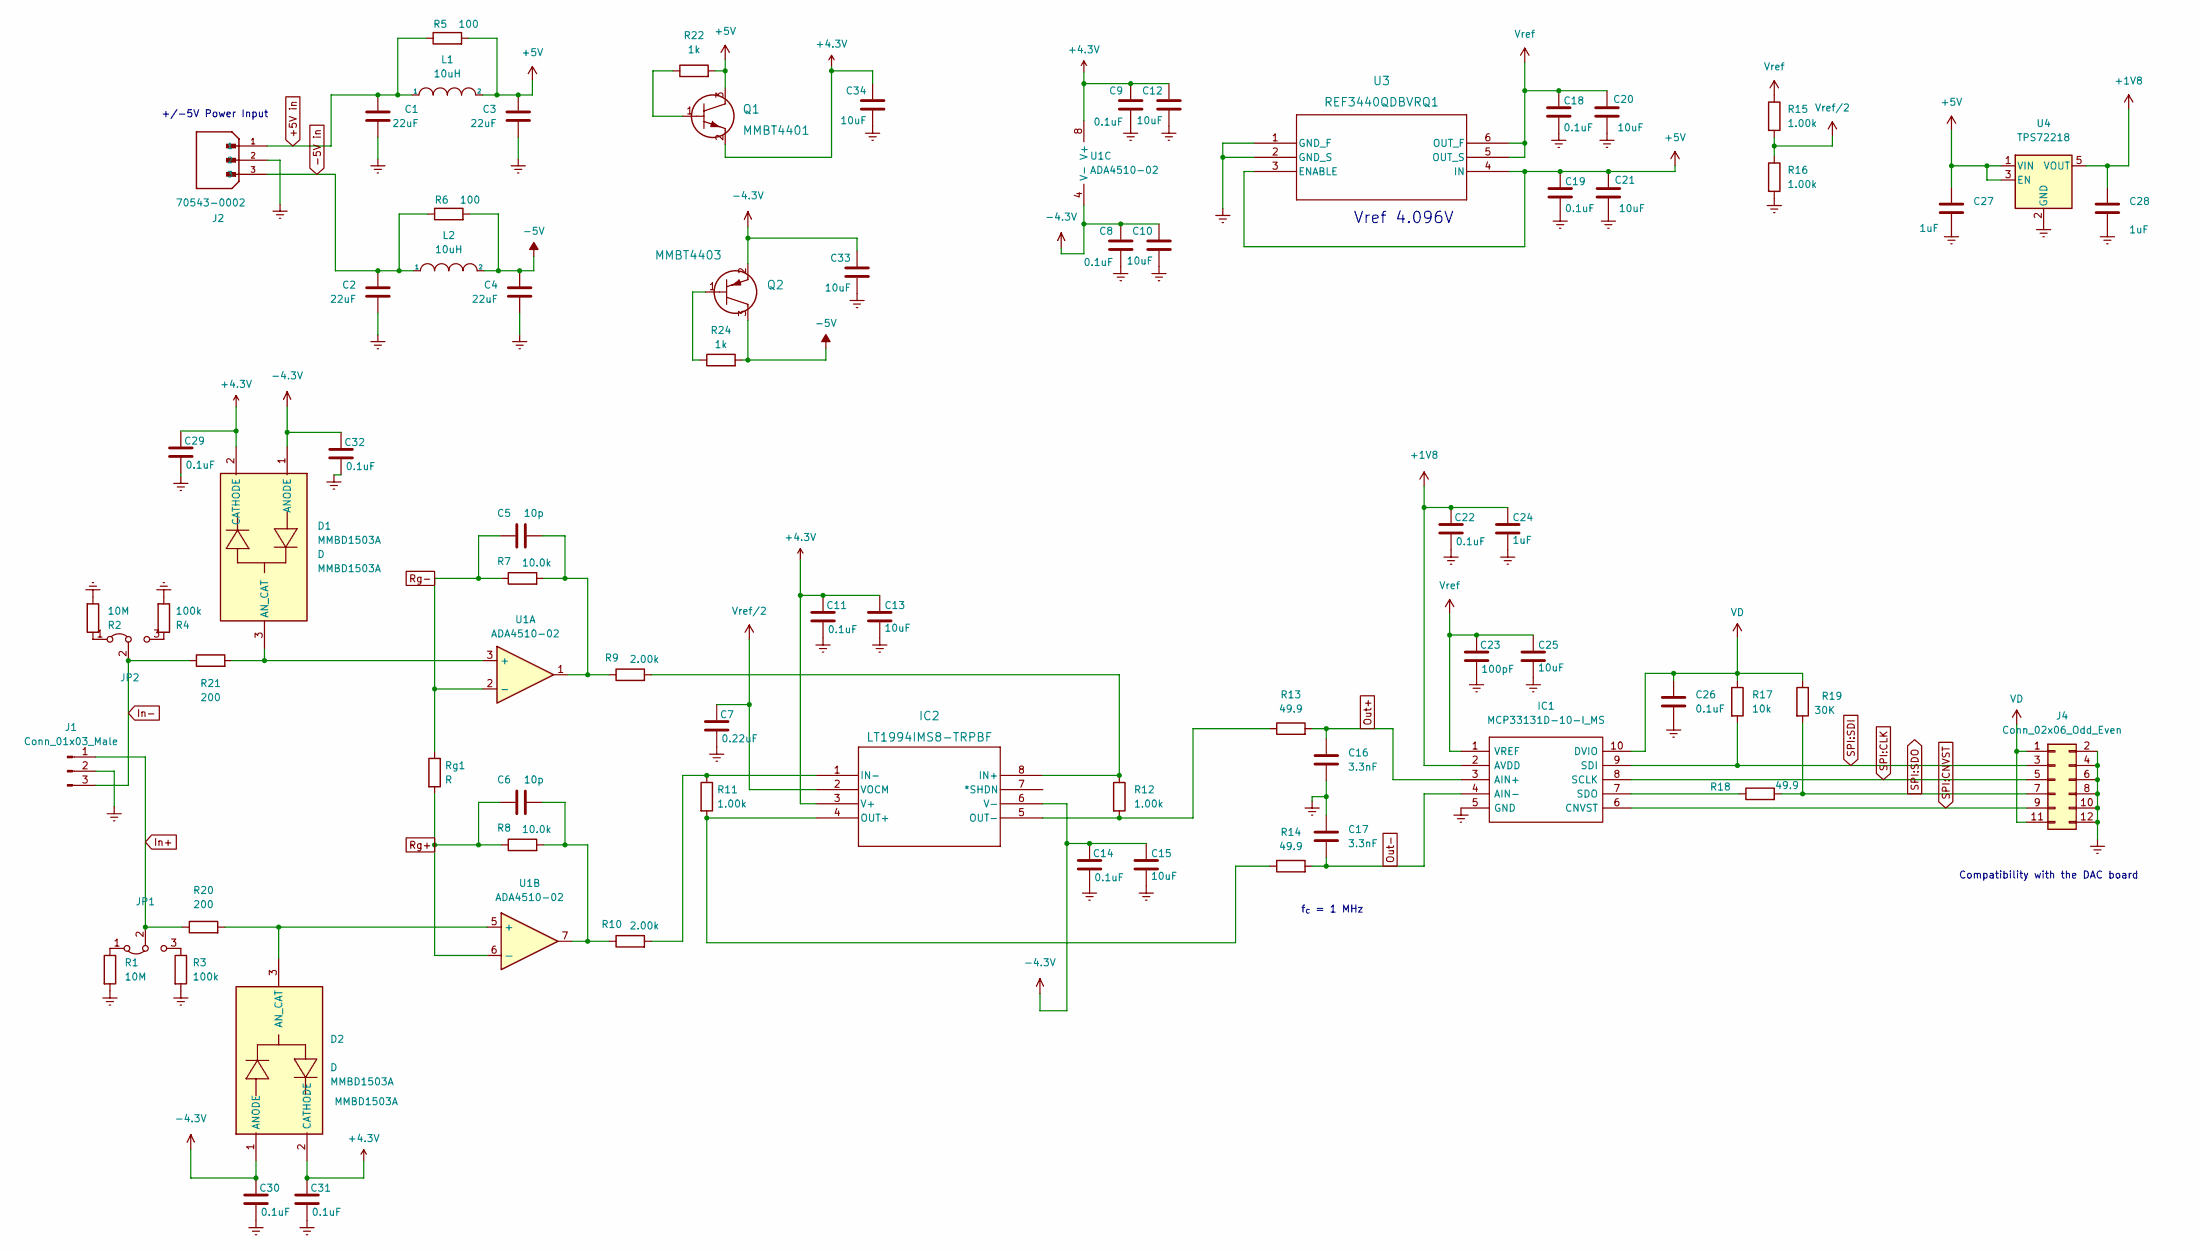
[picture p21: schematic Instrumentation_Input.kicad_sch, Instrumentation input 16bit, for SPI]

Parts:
C1, C2, C3, C4: 22uF; C_0805_2012Metric; Digikey 490-12389-1-ND
C5, C6: 10p; C_0402_1005Metric; Digikey 478-KAQ05ACG1H100FHCT-ND
C7: 0.22uF; C_0402_1005Metric; Digikey 490-10671-1-ND
C8, C9, C11, C14, C18, C19, C22, C26, C29, C30, C31, C32: 0.1uF; C_0402_1005Metric; Digikey 490-6328-1-ND
C10, C12, C13, C15, C20, C21, C25, C33, C34: 10uF; C_0603_1608Metric; Digikey 490-12317-1-ND
C16, C17: 3.3nF; C_0402_1005Metric; Digikey 490-GRM1555C1H332GE01DCT-ND
C23: 100pF; C_0402_1005Metric; Digikey 399-17546-1-ND
C24, C27, C28: 1uF; C_0402_1005Metric; Digikey 490-13339-1-ND
D1, D2: MMBD1503A; SOT-23; Mouser Part Number 512-MMBD1503A
IC1: MCP33131D-10-I_MS; MSOP-10_3x3mm_P0.5mm; Manufacturer_Part_Number MCP33131D-10-I/MS; Mouser Part Number 579-MCP33131D10IMS
IC2: LT1994IMS8-TRPBF; SOIC8_LT1994IMS8-TRPBF_ADI; Digikey 505-LT1994IMS8#PBF-ND
J1: Conn_01x03_Male; PinHeader_1x03_P2.54mm_Vertical; Digikey 3M156268-03-ND
J2: 70543-0002; MOLEX_70543-0002; PARTREV M1; Digikey WM4801-ND
J4: Conn_02x06_Odd_Even; PinHeader_2x06_P2.54mm_Vertical; Manufacturer_Part_Number 929665-02-06-I; Digikey 3M156308-12-ND
JP1, JP2: Conn_01x03_Male; PinHeader_1x03_P1.27mm_Vertical; Manufacturer_Part_Number GRPB031VWVN-RC; Digikey S9014E-03-ND
L1, L2: 10uH; L_Taiyo-Yuden_NR-40xx; Manufacturer_Part_Number 587-2886-1-ND; Digikey 587-2886-1-ND
Q1: MMBT4401; SOT-23_LTO; Digikey 4878-MMBT4401CT-ND
Q2: MMBT4403; SOT-23_LTO; Digikey 4878-MMBT4403CT-ND
R1, R2: 10M; R_0603_1608Metric_Pad0.98x0.95mm_HandSolder; Digikey RMCF0603FT10M0CT-ND
R3, R4: 100k; R_0603_1608Metric_Pad0.98x0.95mm_HandSolder; Digikey P100KHCT-ND
R5, R6: 100; R_0603_1608Metric; Digikey 541-2786-1-ND
R7, R8: 10.0k; R_0402_1005Metric; Digikey RNCF0402BTE10K0CT-ND
R9, R10: 2.00k; R_0402_1005Metric; Digikey 10-ERA-2VEB2001XCT-ND
R11, R12, R15, R16: 1.00k; R_0402_1005Metric; Digikey 738-RNCF0402BTE1K00CT-ND
R13, R14, R18: 49.9; R_0402_1005Metric; Digikey P49.9LCT-ND
R17: 10k; R_0402_1005Metric; Digikey P10.0KLCT-ND
R19: 30K; R_0402_1005Metric; Digikey P30.0KLCT-ND
R20, R21: 200; R_0402_1005Metric; Digikey P200LCT-ND
R22, R24: 1k; R_0402_1005Metric; Digikey P1.00KLCT-ND
Rg1: R; R_Axial_DIN0204_L3.6mm_D1.6mm_P5.08mm_Horizontal
U1: ADA4510-02; SOIC-8_3.9x4.9mm_P1.27mm; Manufacturer_Part_Number ADA4510-2ARZ; Digikey 505-ADA4510-2ARZ-RLCT-ND
U3: REF3440QDBVRQ1; SOT-23-6_TEX; Manufacturer_Part_Number REF3440QDBVRQ1; Digikey 296-53237-1-ND
U4: TPS72218; SOT-23-5; Manufacturer_Part_Number TPS72218DBV (R/T); Digikey 296-27048-1-ND

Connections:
+1V8: C22.1, C24.1, C28.1, IC1.2 (AVDD), U4.5 (VOUT)
+4.3V: C9.1, C11.1, C12.1, C13.1, C29.1, C31.1, C34.1, D1.2 (CATHODE), D2.2 (CATHODE), IC2.3 (V+), Q1.2, U1.8 (V+)
+5V: C3.1, C19.2, C21.1, C27.1, L1.2, Q1.3, R5.2, R22.2, U3.3 (ENABLE), U3.4 (IN), U4.1 (VIN), U4.3 (EN)
+5V in: C1.1, J2.1, L1.1, R5.1
-4.3V: C8.1, C10.1, C14.1, C15.1, C30.1, C32.1, C33.1, D1.1 (ANODE), D2.1 (ANODE), IC2.6 (V-), Q2.2, U1.4 (V-)
-5V: C4.1, L2.2, Q2.3, R6.2, R24.2
-5V in: C2.1, J2.3, L2.1, R6.1
Earth: C1.2, C2.2, C3.2, C4.2, C7.2, C8.2, C9.2, C10.2, C11.2, C12.2, C13.2, C14.2, C15.2, C16.2, C17.1, C18.1, C19.1, C20.2, C21.2, C22.2, C23.2, C24.2, C25.2, C26.2, C27.2, C28.2, C29.2, C30.2, C31.2, C32.2, C33.2, C34.2, IC1.5 (GND), J1.2, J2.2, J4.2, J4.4, J4.6, J4.8, J4.10, J4.12, R1.2, R2.2, R3.2, R4.2, R16.2, U3.1 (GND_F), U3.2 (GND_S), U4.2 (GND)
In+: J1.1, JP1.2 (C), R20.1
In-: J1.3, JP2.2 (C), R21.1
unnamed: C5.2, R7.2, R9.1, U1.1
unnamed: C6.2, R8.2, R10.1, U1.7
unnamed: D1.3 (AN_CAT), R21.2, U1.3 (+)
unnamed: D2.3 (AN_CAT), R20.2, U1.5 (+)
unnamed: IC1.7 (SDO), R18.1
unnamed: IC2.1 (IN-), R10.2, R11.1
unnamed: IC2.4 (OUT+), R11.2, R14.1
unnamed: IC2.5 (OUT-), R12.2, R13.1
unnamed: IC2.8 (IN+), R9.2, R12.1
unnamed: JP1.1 (A), R1.1
unnamed: JP1.3 (B), R3.1
unnamed: JP2.1 (A), R2.1
unnamed: JP2.3 (B), R4.1
unnamed: Q1.1, R22.1
unnamed: Q2.1, R24.1
Out+: C16.1, IC1.3 (AIN+), R13.2
Out-: C17.2, IC1.4 (AIN-), R14.2
Rg+: C6.1, R8.1, Rg1.2, U1.6 (-)
Rg-: C5.1, R7.1, Rg1.1, U1.2 (-)
SPI:CLK: IC1.8 (SCLK), J4.5
SPI:CNVST: IC1.6 (CNVST), J4.9
SPI:SDI: IC1.9 (SDI), J4.3, R17.2
SPI:SDO: J4.7, R18.2, R19.2
VD: C26.1, IC1.10 (DVIO), J4.1, J4.11, R17.1, R19.1
Vref: C18.2, C20.1, C23.1, C25.1, IC1.1 (VREF), R15.1, U3.5 (OUT_S), U3.6 (OUT_F)
Vref/2: C7.1, IC2.2 (VOCM), R15.2, R16.1

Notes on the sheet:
+/-5V Power Input
Vref 4.096V
Compatibility with the DAC board
f_{c} = 1 MHz

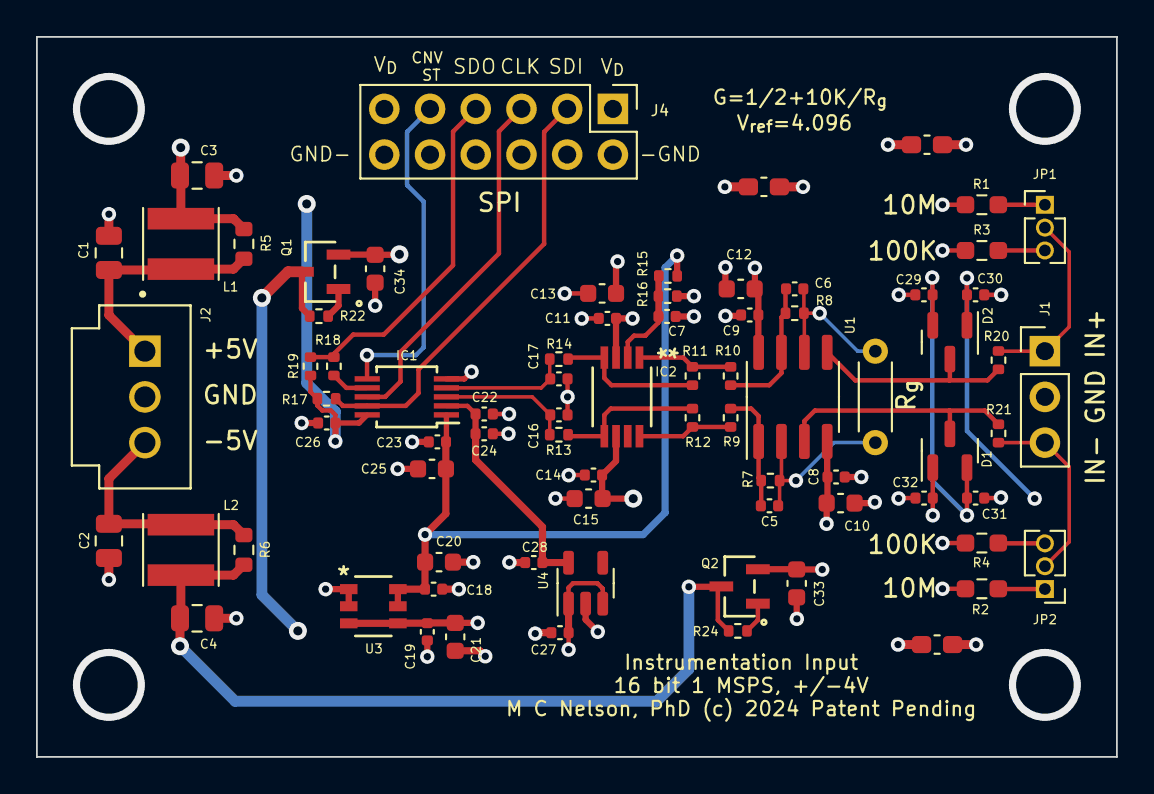
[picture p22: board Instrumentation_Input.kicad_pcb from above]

Board: 4 copper layers, 60.0 x 40.0 mm, 74 parts (0 on the bottom side), 36 nets.

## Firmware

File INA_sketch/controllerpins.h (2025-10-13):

/*
  Author:   Mitchell C. Nelson
  Date:     March 8, 2024
  Contact:  drmcnelson@gmail.com

 */

#ifndef CONTROLLER_PINS_H
#define CONTROLLER_PINS_H

#include "controller_identification.h"


#ifdef IS_TEENSY
#define MAX_ANALOGPINS 10

#elif defined(IS_ARDUINO_UNO)
#define MAX_ANALOGPINS 6

#else
#error "not recognized as a supported board"

#endif

#ifndef LED
#define LED 13
#endif

#ifndef SYNCPIN
#define SYNCPIN 0
#endif


#ifndef SYNCPIN
#define SYNCPIN 0
#endif

#ifndef BUSYPIN
#define BUSYPIN 1
#endif

#ifndef TRIGGERPIN
#define TRIGGERPIN 2
#endif

#ifndef SPAREPIN
#define SPAREPIN 3
#endif

#if defined(ARDUINO_TEENSY40)
#define CNVSTPIN 9
#define CSPIN 9
#endif

#ifndef CNVSTPIN
#define CNVSTPIN 10
#endif

#ifndef CSPIN
#define CSPIN 10
#endif

void reboot();

#define MAXPINS 24
#define ANALOGINPUT 0xF
extern uint8_t pin_modes[MAXPINS];
extern uint8_t pin_states[MAXPINS];

extern uint8_t analog_pins[MAX_ANALOGPINS];
extern uint8_t analog_pins_selection[MAX_ANALOGPINS];
extern uint8_t analog_pins_nselected;
extern double analog_pins_voltages[MAX_ANALOGPINS];
extern unsigned int analog_pins_averages;
extern bool internal_adc_error;

#define INTERNAL_ADC_BITS 12
#define INTERNAL_ADC_RESOLUTION (3.3/4096.)

/* =====================================================
   Pins, these need to be constant to take advantage of
   digitalWriteFast etc.
   They are hard coded in the the .cpp file, because
   of the register level macros
*/
// External trigger, sync 
const int syncPin = SYNCPIN;         // On sample or shutter or start frame or start followed by delay - for desktop N2 laser
const int busyPin = BUSYPIN;         // Gate output pin, goes high during busy (or shutter)
const int interruptPin = TRIGGERPIN; // Trigger input pin
const int sparePin =  SPAREPIN;      // Spare pin for digital output

// ccd clock pins
const int fMPin        = 4;     // Master clock out for CCD's
const int fMPinMonitor = 5;     // Clock monitor

// TCD1304 pins
const int ICGPin       = 6;     // Integration clear gate
const int SHPin        = 7;     // Shift gate

// s11639-01 pins
const int STPin   =  6;         // start pin
const int TRGPin  = 7;          // trig to start conversion
const int EOSPin = 8;           // Spare pin to the sensor board

// SPI interface
const int CSPin = CSPIN;
const int SDIPin = 11;
const int SDOPin = 12;
const int CLKPin = 13;

// ADC specific pin
const int CNVSTPin = CNVSTPIN;

/* ===================================================
   States, not constant
 */

// Pin states
extern int intedgemode;
extern unsigned int busyPinState;
extern unsigned int syncPinState;
extern unsigned int sparePinState;

// Pin Toggle States
extern bool sync_toggled;
extern bool busy_toggled;
extern bool spare_toggled;

// Operational States
extern bool is_attached;
extern bool is_busy;

char *parseInterruptMode( char *s, uint8_t *mode );

char *parsePin(char *s, int *ipin);
char *parsePinU8(char *s, uint8_t *pin);

bool setPinStr(char *s);
bool writePinStr(char *s);
bool togglePinStr(char *s);
bool pulsePinStr( char *s );

void setPinMode(uint8_t pin, uint8_t mode);
void writePin(uint8_t pin, uint8_t istate);
void togglePin(uint8_t pin);
uint16_t readPin(uint8_t pin);

inline void attachInterruptPin( void (*isr)(), int edge );
inline void detachInterruptPin();

inline void toggleBusyPin( );
inline void toggleSyncPin( );
inline void toggleSparePin( );

void pulsePin( unsigned int pin, unsigned int usecs );
void pulsePinHigh( unsigned int pin, unsigned int usecs );
void pulsePinLow( unsigned int pin, unsigned int usecs );

#ifdef IS_TEENSY
inline uint16_t fastAnalogReadPin( uint8_t pin );
inline uint16_t fastAnalogReadChannel( uint8_t channel );
#endif

uint16_t analogReadPin(uint8_t pin);
uint16_t analogReadChannel(uint8_t channel);
double analogReadPinVoltage(uint8_t pin);
double analogReadChannelVoltage(uint8_t channel);
double analogReadPinVoltageAveraged(uint8_t pin, int navgs);
double analogReadChannelVoltageAveraged(uint8_t channel, int navgs);

bool selectAnalogChannels( unsigned int *channels, int nchannels );
double *analogReadSelected( int navgs);
void printAnalogSelected( int navgs );

#ifdef IS_TEENSY
void startSquareWave(uint8_t pin, float frequencyHz);
void stopSquareWave(uint8_t pin);

void startMasterClock(float frequencyHz);
void stopMasterClock( );
#endif

inline const char *boolstr(bool val);
inline const char *modestr( uint8_t mode );
inline const char *edgestr(int mode);
void printPinState_(uint8_t pin);
void printTogglePinState_(uint8_t pin, uint8_t extrastate);
void printPin( const uint8_t pin );
void printPins( );

void controller_pins_setup();

#endif

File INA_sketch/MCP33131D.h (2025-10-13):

/********************************************************
 * @file MCP33131D.h
 * @copyright Copyright (c) 2024 Mitchell C Nelson, PhD
 * @brief A header-only library for the MCP33131D ADC, for Teensy and Arduino
 *
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
 *********************************************************/

#ifndef MCP33131D_H
#define MCP33131D_H

#include <Arduino.h>
#include <SPI.h>

#include "controller_identification.h"

// ==============================
// CPU clock cycles per usec, secs per cycle
#define MCP33131D_CYCLES_PER_USEC (F_CPU / 1000000)
#define MCP33131D_SECS_PER_CYCLE (1./F_CPU)

// nanoseconds to cycles
#define MCP33131D_NANOSECS_TO_CYCLES(n) (((n)*MCP33131D_CYCLES_PER_USEC)/1000)

// ==============================
// CNVSTPIN, can be selected externally
#ifndef MCP33131D_CNVSTPIN
#ifndef CNVSTPIN
#error need to define either MCP33131D_CNVSTPIN or CNVSTPIN before #include MCP33131D.h, consider including controllerpins.h
#endif
#define MCP33131D_CNVSTPIN CNVSTPIN
#endif

#ifndef SYNCPIN
#error need to define SYNCPIN, consider including controllerpins.h
#endif

#ifndef BUSYPIN
#error need to define BUSYPIN, consider including controllerpins.h
#endif

// ==========================================================
#if defined(IS_TEENSY4)

#include <digitalWriteFast.h>
#define MCP33131D_DIGITALREAD(a) digitalReadFast(a)
#define MCP33131D_DIGITALWRITE(a,b) digitalWriteFast(a,b)
#define MCP33131D_DIGITALTOGGLE(a) digitalToggleFast(a)

// ----------------------
#ifdef USETIMERONE
#include <TimerOne.h>

#else
#ifndef USEINTERVALTIMER
#define USEINTERVALTIMER
#endif
static IntervalTimer mcp33131d_timer;

#endif

// ----------------------
#define MCP33131D_SPI_SPEED 30000000
SPISettings spi_settings(MCP33131D_SPI_SPEED, MSBFIRST, SPI_MODE0);   // 30 MHz, reads

#ifndef MCP33131D_TEENSY_FASTSPI
#define MCP33131D_TEENSY_FASTSPI
#endif

#include "imxrt.h"
#include "pins_arduino.h"

static IMXRT_LPSPI_t *lpspi = &IMXRT_LPSPI4_S;

static uint16_t saved_framesz;

static inline uint16_t get_framesz(  IMXRT_LPSPI_t *port ) {
  return (port->TCR & 0x00000fff) + 1;
}

static inline void set_framesz( IMXRT_LPSPI_t *port, uint16_t nbits ) {
  port->TCR = (port->TCR & 0xfffff000) | LPSPI_TCR_FRAMESZ(nbits-1); 
}

static inline uint16_t transfer16( IMXRT_LPSPI_t *port, uint16_t data ) {
  port->TDR = data;                         // output 16 bit data
  while (port->RSR & LPSPI_RSR_RXEMPTY) {}  // wait while RSR fifo is empty
  return port->RDR;                         // return data read
}

#endif

// ==========================================================
#if defined(IS_ARDUINO_UNO_R4)

#define MCP33131D_DIGITALREAD(a) digitalRead(a)
#define MCP33131D_DIGITALWRITE(a,b) digitalWrite(a,b)
#define MCP33131D_DIGITALTOGGLE(a) digitalWrite(a,!digitalRead(a))

#include <elapsedMillis.h>

#define ARM_DWT_CYCCNT DWT->CYCCNT

void setupCYCCNT() {
  CoreDebug->DEMCR |= CoreDebug_DEMCR_TRCENA_Msk;
  ITM->LAR = 0xc5acce55;
  DWT->CYCCNT = 0;
  DWT->CTRL |= DWT_CTRL_CYCCNTENA_Msk;
}


#ifdef USEINTERVALTIMER
#error INTERVALTIMER not available for UNO R4
#endif

#ifndef USETIMERONE
#define  USETIMERONE
#endif
#include <TimerOne.h>

//#define MCP33131D_SPI_SPEED 12000000
#define MCP33131D_SPI_SPEED 24000000
SPISettings spi_settings(MCP33131D_SPI_SPEED, MSBFIRST, SPI_MODE0);   // 30 MHz, reads

//#define MCP33131D_UNOR4_SLOWSPI
#define MCP33131D_UNOR4_FASTSPI

#endif

// ==========================================
// Define signed or unsigned, not both
#if defined(MCP33131D_SIGNED) && defined(MCP33131D_UNSIGNED)
#error need to define either MCP33131D_SIGNED or MCP33131D_UNSIGNED, not both
#endif

// Default to signed
#if !defined(MCP33131D_SIGNED) && !defined(MCP33131D_UNSIGNED)
#define MCP33131D_SIGNED
#endif

// ==========================================
// Scaling
#ifndef MCP33131D_VFS
#define MCP33131D_VFS 8.0
#endif

// Binaryscale
#if defined(MCP33131D_SIGNED)
#define MCP33131D_BFS 32768
#elif defined(MCP33131D_UNSIGNED)
#define MCP33131D_BFS 65536
#endif

// Precision, volts per LSB
#ifndef MCP33131D_LSB
#define MCP33131D_LSB ((float)MCP33131D_VFS/MCP33131D_BFS)
#endif

// binary to volts
#define MCP33131D_VOLTS(a) ((mcp33131d_t)a*MCP33131D_LSB)

// Data represenation (type)
#if defined(MCP33131D_SIGNED)
typedef int16_t mcp33131d_t;
typedef int32_t mcp33131d_sum_t;
#elif defined(MCP33131D_UNSIGNED)
typedef uint16_t mcp33131d_t;
typedef uint32_t mcp33131d_sum_t;
#endif

#define MCP33131D_FORMAT_BINARY 0
#define MCP33131D_FORMAT_ASCII 1
#define MCP33131D_FORMAT_VOLTS 2

// ==========================================
// MCP33131D timing

#define MCP33131D_MIN_CLOCK_USECS 5

#define MCP33131D_ACQUIRE_NANOSECONDS 300
#define MCP33131D_WAIT_ACQUIRE MCP33131D_NANOSECS_TO_CYCLES(MCP33131D_ACQUIRE_NANOSECONDS)

#if defined(IS_ARDUINO_UNO_R4)
#define MCP33131D_WAIT_CONVERSION MCP33131D_NANOSECS_TO_CYCLES(50)

#elif defined(MCP33131D_TEENSY_FASTSPI)
#define MCP33131D_WAIT_CONVERSION MCP33131D_NANOSECS_TO_CYCLES(650)

#elif defined(IS_TEENSY4)
#define MCP33131D_WAIT_CONVERSION MCP33131D_NANOSECS_TO_CYCLES(580)

#else
#error "controller board type not defined, UNOR4 or Teensy"

#endif


// ==================================================================
static void printCounter( const char *s, unsigned int counter, unsigned int knts, bool eol=true )
{
  Serial.print(s);
  Serial.print(" "); Serial.print(counter);
  Serial.print( " / " ); Serial.print( knts );
  if(eol) Serial.println("");
}

bool pointermatch( void (*f)(), void (*g)() )

{
  return (f == g) ? true : false;
}

uint64_t cycles64( )
{
  static uint32_t oldCycles = ARM_DWT_CYCCNT;
  static uint32_t highDWORD = 0;

  uint32_t newCycles = ARM_DWT_CYCCNT;

  if (newCycles < oldCycles) {
    ++highDWORD;
  }
  oldCycles = newCycles;
  
  return (((uint64_t)highDWORD << 32) | newCycles);
}

/******************************************************************
 * @brief The MCP33131D class
 *
 */

class MCP33131D
{
  
public:  
  uint32_t elapsed_cycles_holder = ARM_DWT_CYCCNT;

  uint16_t format = 0;

  //  inline static uint32_t cyccnt_holder;
  inline static uint64_t cyccnt_holder64;

  inline static bool verbose;

  inline static bool errorflag;
  
  inline static mcp33131d_t *buffer;
  inline static mcp33131d_t *buffer_next;
  inline static unsigned int buffer_length;
  inline static unsigned int buffer_counter;
  inline static void (*buffer_callback)();

  inline static uint8_t watched_pin;
  inline static uint8_t watched_edge;
  
  inline static unsigned int frame_counter;
  inline static unsigned int frame_knts;

  inline static mcp33131d_t single_val;
  inline static unsigned int single_knts;
  inline static unsigned int single_counter;
  inline static void (*single_callback)();
  inline static unsigned int single_cyccnt;
  
  inline static mcp33131d_sum_t sum_val;
  inline static unsigned int sum_counter;
  inline static unsigned int sum_knts;
  inline static void (*sum_callback)();

  inline static unsigned int clock_counter;
  inline static unsigned int clock_knts;
  //inline static unsigned int clock_usecs;
  inline static unsigned long clock_usecs;
  inline static bool clock_active;
  inline static void (*clock_isr)();
  //inline static uint32_t clock_cyccnt;
  //inline static uint32_t clock_cyccnt_holder;
  inline static uint64_t clock_cyccnt_holder64;

  inline static unsigned int interrupt_counter;
  inline static unsigned int interrupt_knts;
  inline static uint8_t interrupt_pin;
  inline static uint8_t interrupt_mode;
  inline static bool interrupt_active;
  inline static void (*interrupt_isr)();
  //inline static uint32_t interrupt_cyccnt;
  //inline static uint32_t interrupt_cyccnt_holder;
  
  inline static uint64_t interrupt_cyccnt_holder64;
  
  // -------------------------------------
    
  MCP33131D()
  {
  }
    
  ~MCP33131D( )
  {
  }

  void begin()
  {
#ifdef IS_ARDUINO_UNO_R4
    setupCYCCNT();
#endif
    
    // SPI setup for the MCP33131D (ADC)
    pinMode(MCP33131D_CNVSTPIN, OUTPUT);
    MCP33131D_DIGITALWRITE(MCP33131D_CNVSTPIN, LOW);
  
    SPI.begin();
    SPI.beginTransaction(spi_settings);

    Serial.print("MCP33131D start SPI, CS pin ");
    Serial.println(MCP33131D_CNVSTPIN);
    
#ifdef MCP33131D_TEENSY_FASTSPI
    saved_framesz = get_framesz( lpspi );
    set_framesz( lpspi, 16 );
#endif
    
#ifdef MCP33131D_UNOR4_FASTSPI
    SPI.transfer16_setup();
#endif
    

#ifdef USETIMERONE
    Timer1.initialize(100000);
    delay(1000);
    Timer1.stop();
#endif

  }

  void end()
  {
#ifdef MCP33131D_TEENSY_FASTSPI
    set_framesz( lpspi, saved_framesz );
#endif

#ifdef MCP33131D_UNOR4_FASTSPI
    SPI.transfer16_cleanup();
#endif
    
    SPI.endTransaction();
    SPI.end();
  }

  bool error()
  {
    bool saveflag = errorflag;
    errorflag = false;
    return saveflag;
  }

  void printConfiguration( )
  {
    Serial.print("Configuration: MCP33131D (16 bit differential ADC)");
#ifdef MCP33131D_SIGNED
    Serial.print(" read_as signed");
#endif
#ifdef MCP33131D_UNSIGNED
    Serial.print(" read_as unsigned");
#endif
    Serial.print(" bits 16");
    Serial.print(" vfs "); Serial.print(MCP33131D_VFS,6);
    Serial.print(" volts_per_lsb "); Serial.print(MCP33131D_LSB,6);
    Serial.println("");
  }
  
  /* ========================================
     Basic read function
  */
  static mcp33131d_t read( )
  {
    uint16_t u16;

    uint32_t raw_cycles_holder = ARM_DWT_CYCCNT;

    // Start the ADC conversion, data is ready 730nsec later.
    MCP33131D_DIGITALWRITE( MCP33131D_CNVSTPIN, HIGH );

    // Wait for the conversion time
    while((ARM_DWT_CYCCNT-raw_cycles_holder) < MCP33131D_WAIT_CONVERSION);
    
    // Enable readout
    MCP33131D_DIGITALWRITE( MCP33131D_CNVSTPIN, LOW );
    
#if defined(MCP33131D_TEENSY_FASTSPI)
    u16 = transfer16(lpspi,0xFFFF);

#elif defined(MCP33131D_UNOR4_SLOWSPI)
    u16 = SPI.transfer16_asbytes(0xFFFF);

#elif defined(MCP33131D_UNOR4_FASTSPI)
    u16 = SPI.transfer16_transfer(0xFFFF);    

#else
    u16 = SPI.transfer16(0xFFFF);

#endif
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

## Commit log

2025-01-30 Initial KiCAD upload
    [Instrumentation_Input.kicad_pcb, Instrumentation_Input.kicad_sch]
2025-10-13 Pin assignment for R3 controller

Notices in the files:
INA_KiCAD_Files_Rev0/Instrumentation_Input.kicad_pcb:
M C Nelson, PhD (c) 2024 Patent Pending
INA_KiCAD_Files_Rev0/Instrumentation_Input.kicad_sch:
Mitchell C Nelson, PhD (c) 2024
